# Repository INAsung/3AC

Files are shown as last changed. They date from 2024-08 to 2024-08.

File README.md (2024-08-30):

# Three-alternative forced choice task (3AC)

### *Low cost implementation of three-alternative forced choice task with Arduino mega 2560 &amp; 3D printing*

KakaoTalk_20240830_165530499

---
### *What is 3AC?*
그림1

- 3AC is extended version of conventional two-alternative forced choice task. 
- 3AC task comprises two phases:
	- i) blind tasting of either a pure tastant or mixture (e.g., sweet, salty, or sweet-salty mixture)
	- ii) selection of one of the three bottles corresponding to the tasted solution.

- **A servo motor** switches the tastant solution provided to the mouse for each trial. The liquids are never mixed because they flow through separate lines.
- **Linear actuators** move back and forth, allowing the mouse access to the lick spout for a limited time period.
- **DIY capacitive lickometer** detects and records licks.

- *This is the **first attempt** to match three choices to the three decision spouts.*
---

### *This repository includes:*
- Whole Arduino codes and 3D printing schematics for implementing 3AC behavioral apparatus
- Imaged guideline for making DIY capacitive sensor
- You can use this project for any task that requires the mouse to identify one of three possible options. (though, I developed it for a study on *taste mixture identification*.

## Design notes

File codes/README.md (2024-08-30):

# Description for task schedule and following Arduino codes

- ❗ You have to install additional Arduino libraries: **CapacitiveSensor (v 0.5.1)**, **Keypad (v 3.1.1)**
- **You should read each .ino files carefully and change each parameters as you want.** (pinmaps, servo motor's reducer ratio and encoder resolution, training schedules,  etc)

- **Tip for preventing choice bias**: Mice tend to lick the closest spout, so each spouts should be placed equally distant from target position.

- from stage3, I added keypad codes for convenience. (refer to code)
---

|name | explanation |expected period|
|:--:|:--:|:--:|
|stage1 |only central spouts move, give water unconditionally | 1~2 days|
|stage2 | only lateral spouts move, give water when lick is detected (choice should be counterbalanced) | 3 days
|stage3 |both lateral spouts and central spout move. give water when lick is deteced (choice should be counterbalanced) |5~7 days
|stage4|central spout come in and give water unconditionally. then, both lateral spouts and central spout come in and give water when lick is detected|1~2 days
|stage5 (semi-3AC)|easy version of 3AC. Sampling liquid does not change until the mouse makes three consecutive right choices or ten right choices.|3~4 weeks
|stage6 (real 3AC)| now, let's start 3AC task! (sampling liquid will be randomized for each trials) | 1 week

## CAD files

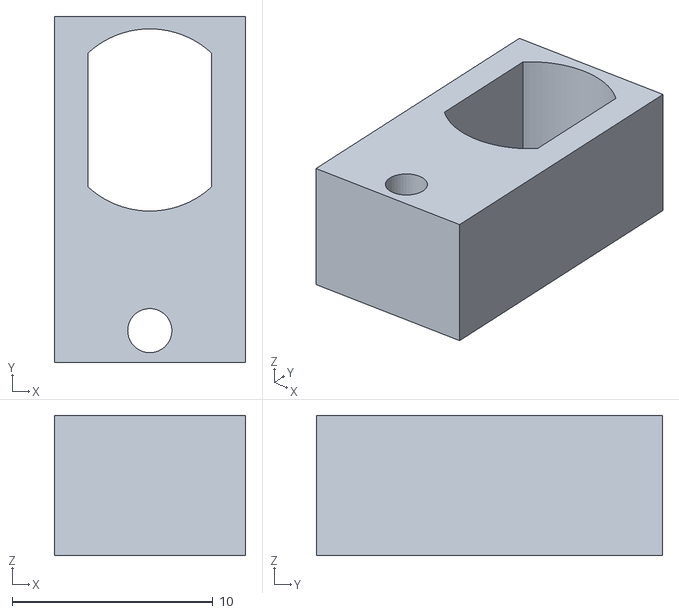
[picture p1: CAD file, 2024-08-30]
assembly/accessory/LATERAL_HOLDER.stl
9.52 x 17.3 x 7.00

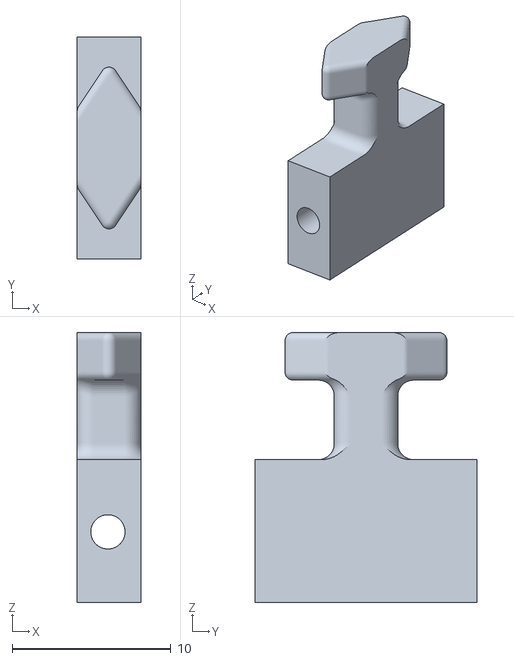
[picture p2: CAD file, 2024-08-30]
assembly/essential/CENTRAL_SAMPLING_HOLDER_SHORT.stl
4.00 x 14.0 x 17.0

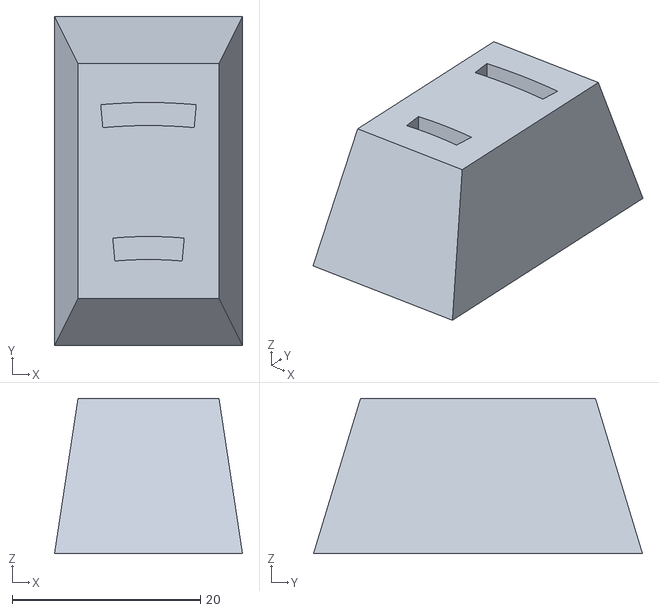
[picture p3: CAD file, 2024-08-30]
assembly/accessory/SPOUT_SELECTOR_SUPPORT_EXTENDER.stl
20.0 x 35.0 x 16.5

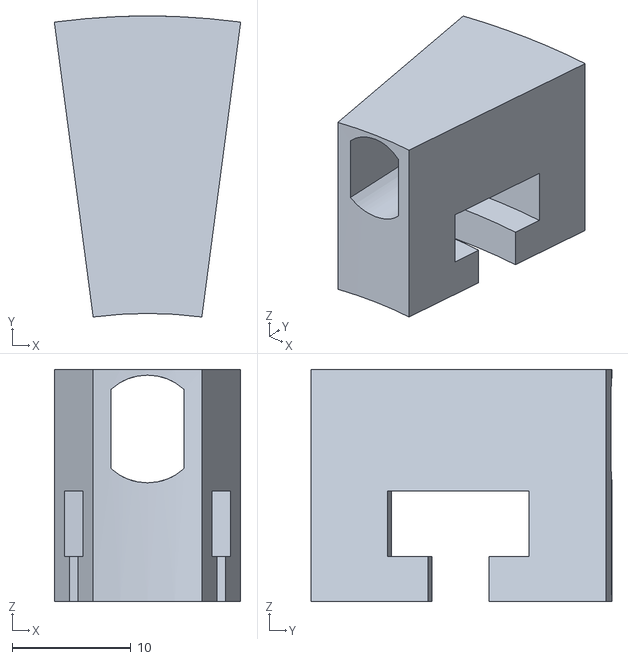
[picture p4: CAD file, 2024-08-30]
assembly/essential/MOTOR_CONNECTOR_THICK.stl
15.7 x 25.3 x 19.5

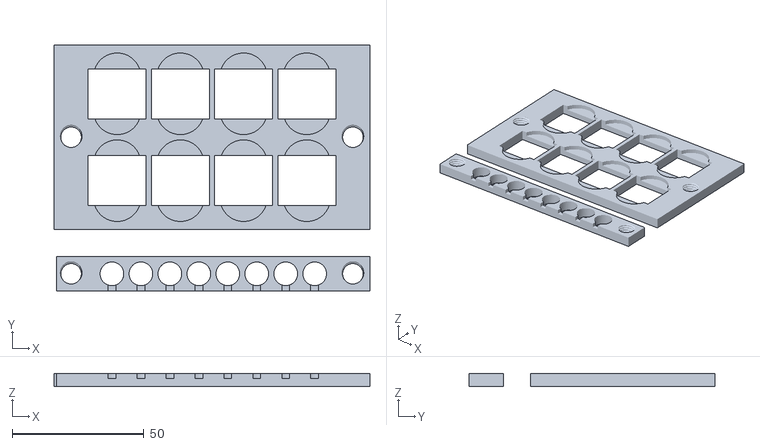
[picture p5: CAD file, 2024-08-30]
assembly/accessory/HOLDERS.stl
120.0 x 93.4 x 5.00

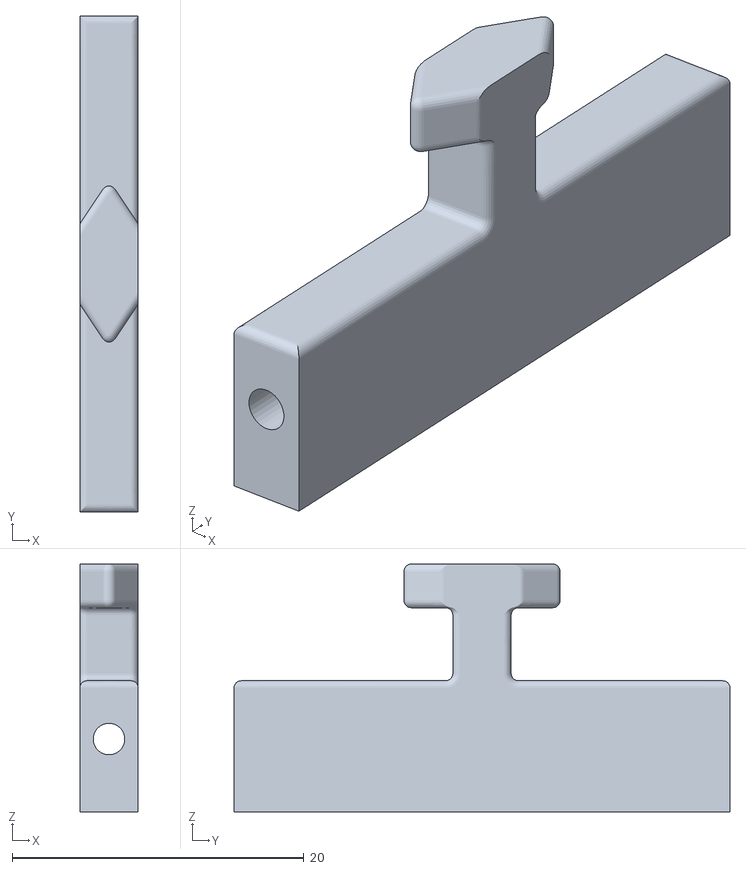
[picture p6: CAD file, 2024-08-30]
assembly/essential/CENTRAL_SAMPLING_HOLDER_LONG.stl
4.00 x 34.0 x 17.0

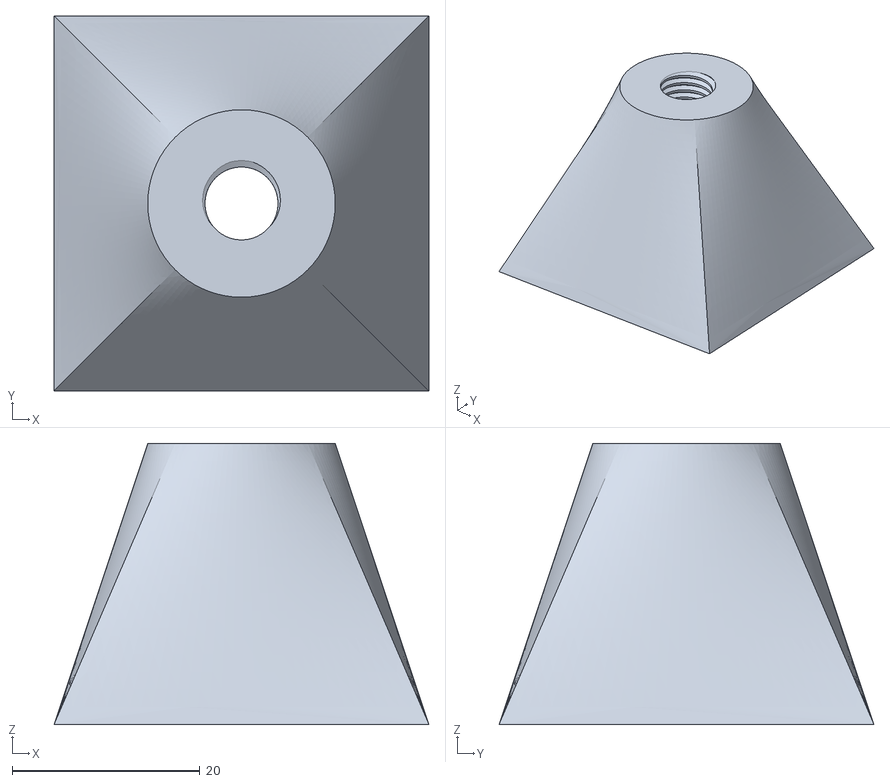
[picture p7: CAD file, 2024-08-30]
assembly/accessory/BASE.stl
40.0 x 40.0 x 30.0

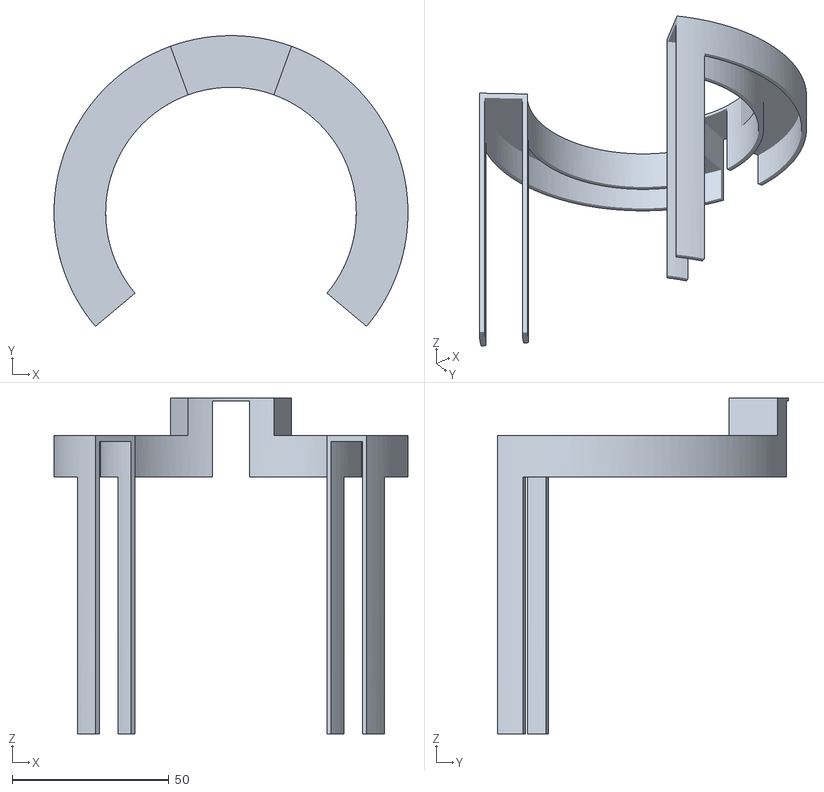
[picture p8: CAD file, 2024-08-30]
assembly/essential/SPOUT_SELECTOR_SUPPORT_THIN.stl
113.0 x 92.8 x 107.2

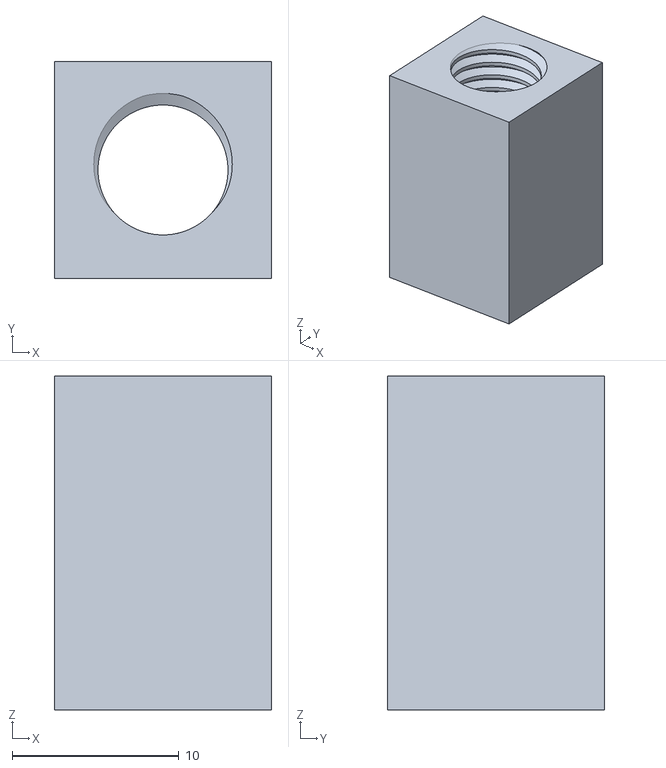
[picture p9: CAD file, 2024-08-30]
assembly/accessory/NAIL_EXTENDER.stl
13.0 x 13.0 x 20.0

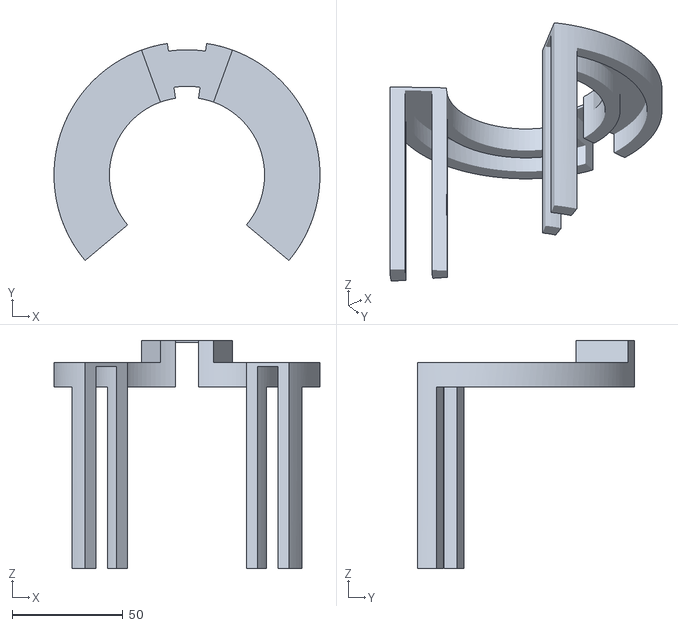
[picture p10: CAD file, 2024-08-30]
assembly/essential/SPOUT_SELECTOR_SUPPORT_THICK.stl
120.0 x 97.9 x 103.0

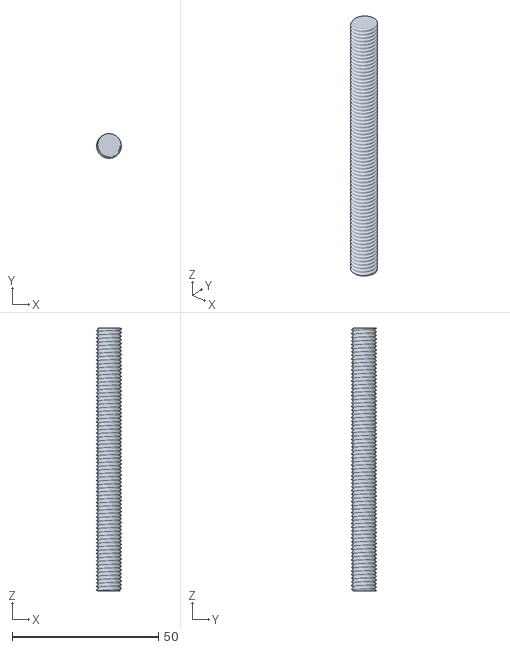
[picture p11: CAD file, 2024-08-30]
assembly/accessory/NAIL_90mm.stl
8.47 x 8.47 x 90.0

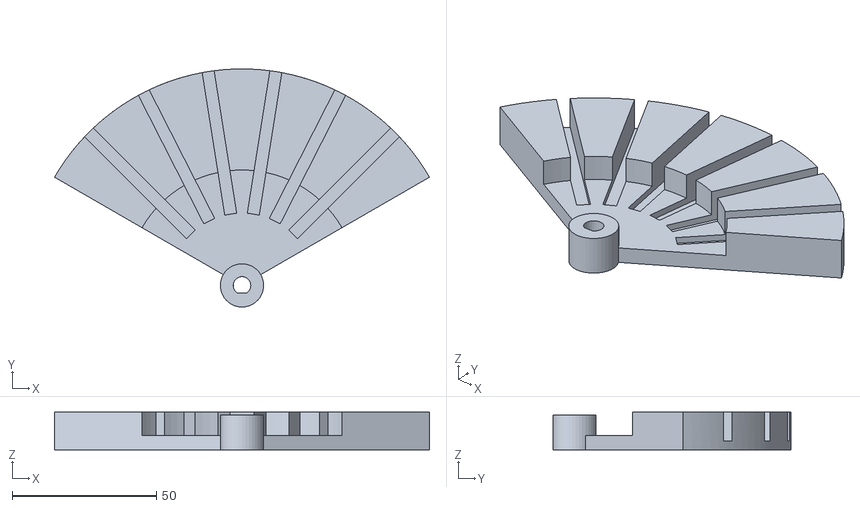
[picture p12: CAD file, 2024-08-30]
assembly/essential/SPOUT_SELECTOR_SHORT.stl
129.9 x 82.5 x 13.0

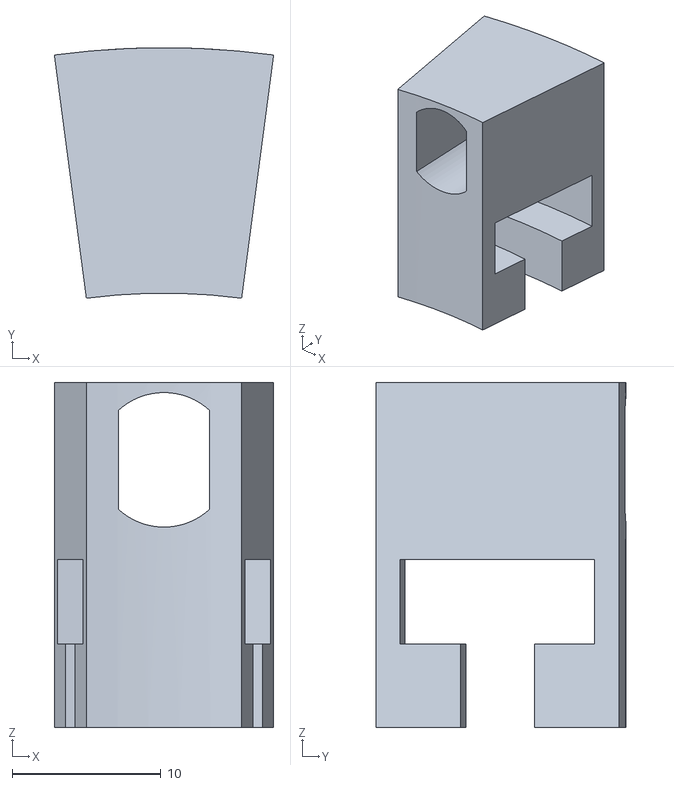
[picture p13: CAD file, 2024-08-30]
assembly/essential/MOTOR_CONNECTOR_THIN.stl
14.7 x 16.8 x 23.2

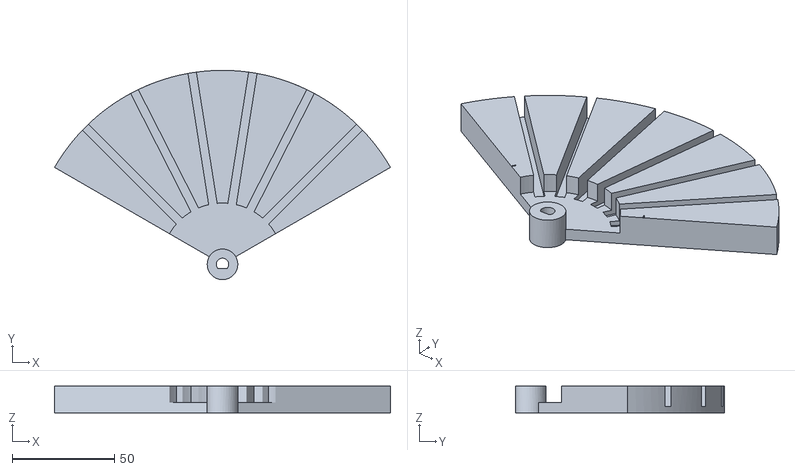
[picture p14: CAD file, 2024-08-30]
assembly/essential/SPOUT_SELECTOR_LONG.stl
164.5 x 102.5 x 13.0

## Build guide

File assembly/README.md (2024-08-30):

# Description for behavioral apparatus assembly & 3D printing

## General info

very grateful to Seoul National University Hadong idea factory...

+ 3D printing machine: one of 3D WOX DP200, DP103 or 2X
+ layer: 0.15mm 
+ program: Autodesk Fusion, 3DWOX Desktop x64

❗ proper post-processing is required. (I mostly used sand paper and soldering iron)

💡 If you need .f3d file, please contact.

📃 **The PDF file includes assembly images and detailed instructions for a simple capacitive lickometer.**

## What you need

### Key devices
|name|for what?|ea.|note|
|:---:|:---:|:---:|:---:|
|arduino mega 2650|main controller|1||
|linear actuator|liquid delivery|4|100mm range, 15mm/s model. I bought it from AliExpress, so I don't know exact model name|
|RB-35GM W/EC|servo motor with encoder for spout selection|1|https://www.dnjmall.com/goods/goods_list.php?cateCd=009|
|LHDA1231115H|solenoid valve for liquid control|10|from The LEE company|
|GJ-5FA-L [SY-SSR01]|DC to DC SSR for liquid control|10||
|L293D(DIP)|motor driver for linear actuator|3||

In addition, you will need enough amount of blunt needle(liquid spout for mouse), silicon tubing, arduino 4*4 keypad (for convenience), 2M ohmn resistors(for manual lickometer), and 12V DC power supply.

## Assembly
I mostly used **blu tack** for overall assembly.

- **Essential folder** contains essnetial parts for spout selection and delivery
  - There are thin/thick, long/short versions. (schematics are same, only length is different.)
  - I used thin and short versions, but newly made long and thick version to add precision.
  - It is okay to use thin and short versions, but if there occurs some errors, please consider long and thick versions. 

- **Accessory folder** contains liquid delivery tower, motor supporter, etc.

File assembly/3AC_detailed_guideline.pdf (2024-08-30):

## 1. Simple capacitive lickometer

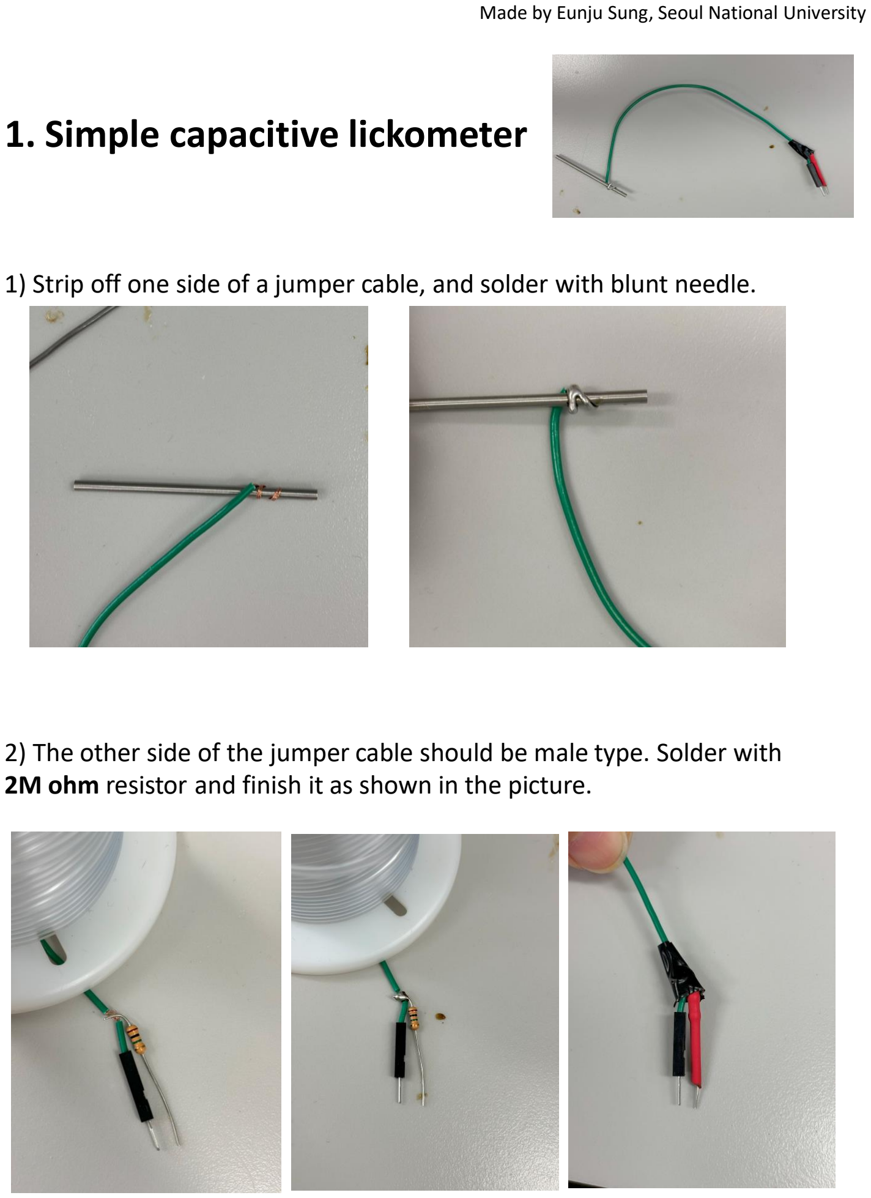
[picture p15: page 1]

Made by Eunju Sung, Seoul National University

1) Strip off one side of a jumper cable, and solder with blunt needle.
2) The other side of the jumper cable should be male type. Solder with 2M ohm resistor and finish it as shown in the picture.

### 1) Overall assembly

## 2. Behavioral apparatus assembly

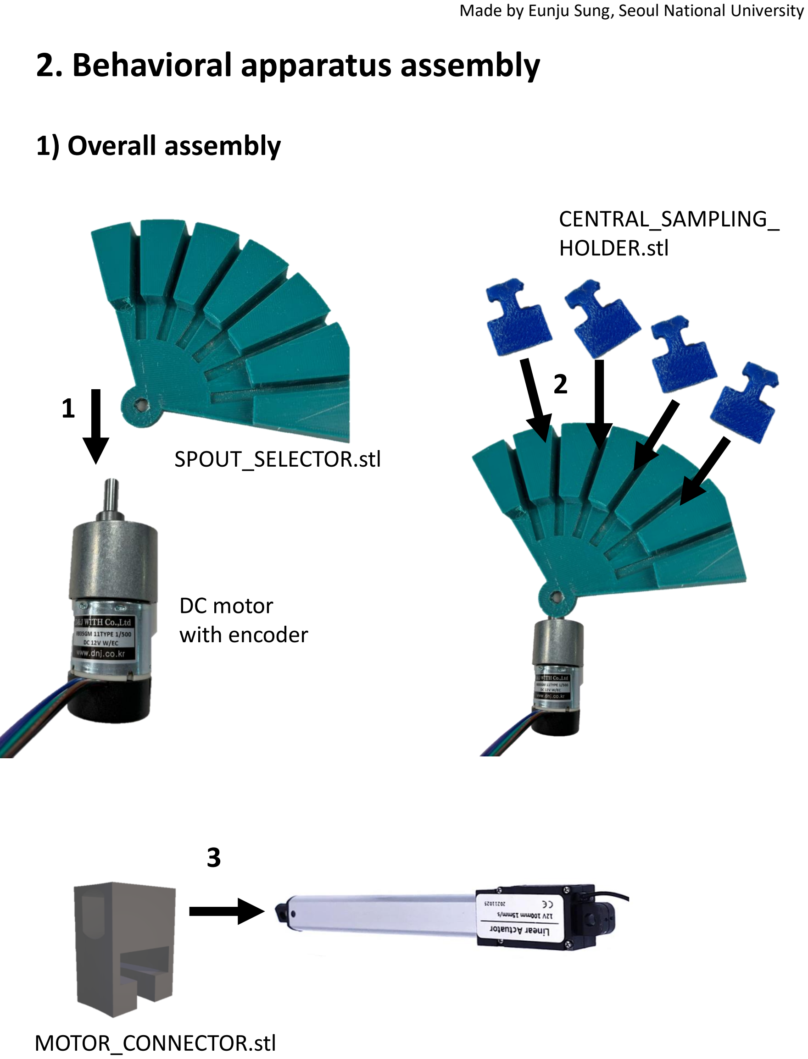
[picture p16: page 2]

1

DC motor
with encoder

SPOUT_SELECTOR.stl

2

CENTRAL_SAMPLING_
HOLDER.stl

3

MOTOR_CONNECTOR.stl

4

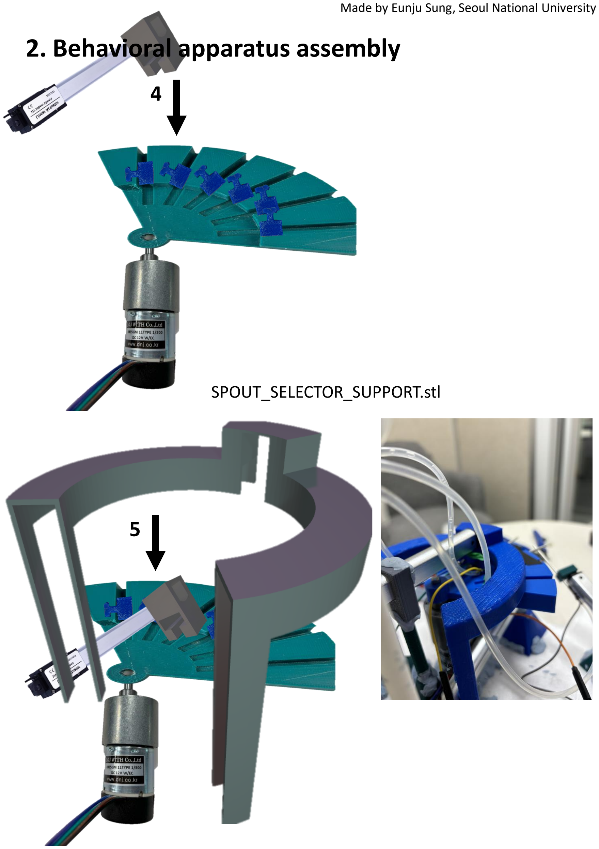
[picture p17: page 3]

SPOUT_SELECTOR_SUPPORT.stl

5

### 6. Place lateral motors and

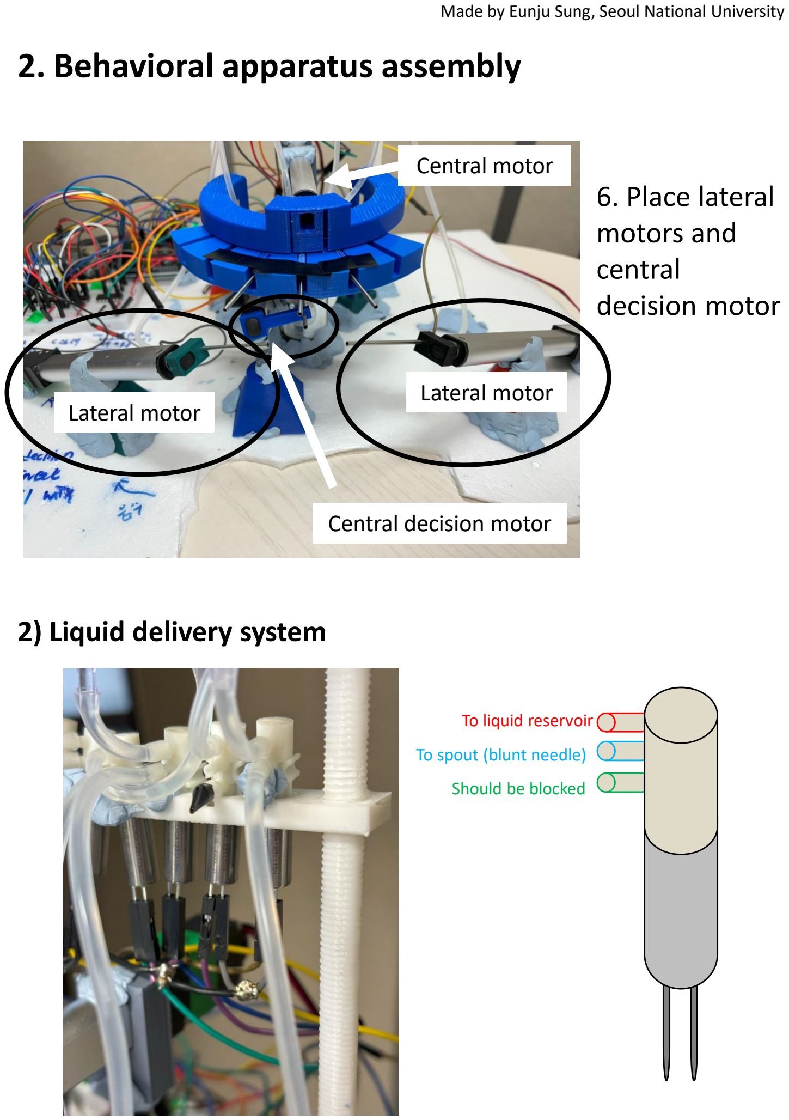
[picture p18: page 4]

### 2) Liquid delivery system

To liquid reservoir

Should be blocked

To spout (blunt needle)

### central decision motor

Lateral motor

Lateral motor

Central decision motor

Central motor

### 3) Spout location

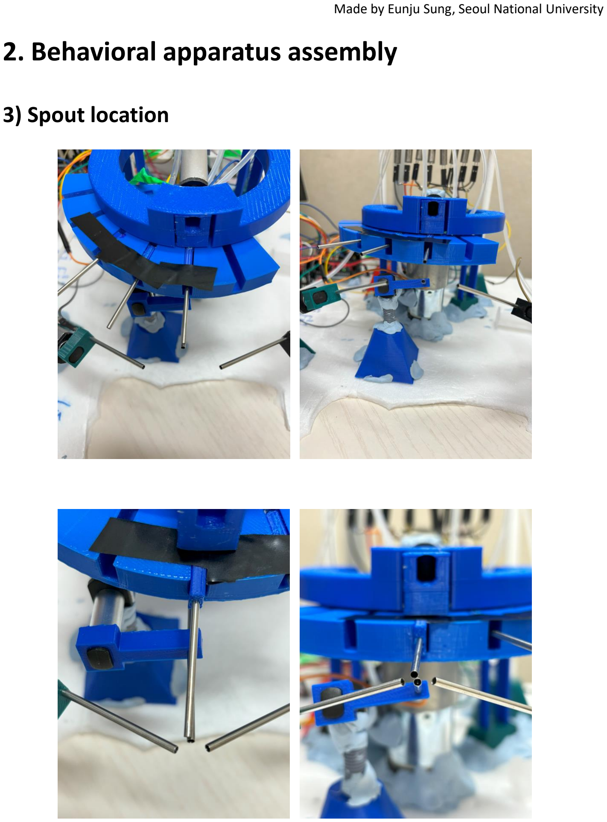
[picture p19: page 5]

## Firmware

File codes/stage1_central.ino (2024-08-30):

#include <CapacitiveSensor.h>

// source code for 3 alternative choice task
// you have to define all configurations according to your setup
// before get started, you must have to calibrate lickometer and motor extension length
// for lickometer calibration, set 'print_lickometer_raw' true and set status -1. Then, see each spout's value, determine float central_threshold[6] & lateral_threshold[2].

// made by Eunju Sung

//////////////// pinmap configurations ////////////////////
// motors (output)
const int lateral1A = 22 ;
const int lateral1B = 23 ;
const int lateral2A = 24 ;
const int lateral2B = 25 ;
const int centralA = 26 ;
const int centralB = 27 ;
const int steppin = 28 ;
const int dirpin = 29;

// solenoid valve control (output)
const int lateral_valve1 = 14;
const int lateral_valve2 = 15;
const int central_valve1 = 16;
const int central_valve2 = 17;
const int central_valve3 = 18;
const int central_valve4 = 19;
const int central_valve5 = 20;
const int central_valve6 = 21;

// lickometers (input)
// smaller number - resistor (red line) / bigger number - wire
const int lickL1A = 38;
const int lickL1B = 39;
const int lickL2A = 40;
const int lickL2B = 41;
const int lick1A = 42;
const int lick1B = 43;
const int lick2A = 44;
const int lick2B = 45;
const int lick3A = 46;
const int lick3B = 47;
const int lick4A = 48;
const int lick4B = 49;
const int lick5A = 50;
const int lick5B = 51;
const int lick6A = 52;
const int lick6B = 53;
CapacitiveSensor lickL1 = CapacitiveSensor(lickL1A, lickL1B);
CapacitiveSensor lickL2 = CapacitiveSensor(lickL2A, lickL2B);
CapacitiveSensor lick1 = CapacitiveSensor(lick1A, lick1B);
CapacitiveSensor lick2 = CapacitiveSensor(lick2A, lick2B);
CapacitiveSensor lick3 = CapacitiveSensor(lick3A, lick3B);
CapacitiveSensor lick4 = CapacitiveSensor(lick4A, lick4B);
CapacitiveSensor lick5 = CapacitiveSensor(lick5A, lick5B);
CapacitiveSensor lick6 = CapacitiveSensor(lick6A, lick6B);
CapacitiveSensor lateral_lickometers[2] = {lickL1, lickL2};
CapacitiveSensor central_lickometers[6] = {lick1, lick2, lick3, lick4, lick5, lick6};
//////////////////////////////////////////////////////


//////////////// output flags  ////////////////////
int status= 0; // -1 for lickometer calibration, 0 for training
bool print_lickometer_raw = true; // for lickometer calibration ## don't set it false. lickometers go wrong..
//////////////////////////////////////////////////////////////


//////////////// training configurations ////////////////////
// spout setting
const int central_reward = 3; // index from zero. spout for central decision
const int central_reward_pin = 19; // see above pinmap
bool lateral_enabled[2] = {false, false};
bool central_enabled[6] = {false, false, false, true, false, false};// do not set true for central_reward spout
const int lick_refractory_tick = 2; // cannot detect new lick for {lick_refractory_tick} ticks (sometimes capsense report single touch as two touch...)
const int capsensor_sensitivity = 40;
float central_threshold[6] = {50, 50, 80, 80, 50, 50};
float lateral_threshold[2] = {100, 50};
const float threshold_default = 10000000;

// trial schedule (unit: milli sec)
const int trial = 60; // number of trial in one session
const float ready2go = 5*1e3;
const float ITI = 15*1e3;
const float valveopen = 0.05*1e3;
const float valve2valve = 0.2*1e3;
const int samplingnum = 1; // give reward 'rewardnum' times, time gap between each delivery is 'valve2valve' 
const float sampling_offset = 0.5*1e3; // time for delay between spout extrude and sampling liquid delivery
const float central_ex = 1.5*1e3; // should be measured according to the distance you want to extrude
const float central_in = 1.6*1e3; // should be measured according to the distance you want to extrude
const float lateral_ex = 1.5*1e3; // should be measured according to the distance you want to extrude
const float lateral_in = 1.5*1e3; // should be measured according to the distance you want to extrude
int bottle_select_step = 160;// for 18 degree
const float start2central_in = 0*1e3;
///////////////////////////////////////////////////////

// 1. start, wait for start2central_in
// 2. central motor start to go forward, motor on for central_ex
// 3. give water unconditionally. valve open for valveopen
// 4. central motor goes back, motor on for central_in

//////// trial parameters (renewed every trial) ////////
unsigned long status_start_time = 0;
unsigned long trial_start_time = 0;
unsigned long now_time = 0;
int trial_count = 1;
int sampling_count = 0;
unsigned long time_consumed = 0; // time consumed for moving step motor (spout selection) 

struct Result{
  bool lickstarted = false;
  bool nowlick = false;
  long lickthres = threshold_default;
  int tick2lick = -1;
};

Result central_lick_status[6];
Result lateral_lick_status[2];
long central_vals_now[6] = {0};
long lateral_vals_now[2] = {0};
long central_vals_prev[6] = {0};
long lateral_vals_prev[2] = {0};
int central_lick_cnt[6] = {0};
int lateral_lick_cnt[2] = {0};
float central_prev_lick_started[6] = {0};
float lateral_prev_lick_started[2] = {0};
//////////////////////////////////////////////////////



////////////  define utility functions  //////////////
void delay_sec(int delay_millisec){
  delay(delay_millisec * 1000);
}

void trial_printer(int trial_count, unsigned long now_time){
  Serial.println("");
  Serial.println("////////////////////////////////////////////////////////////////////////////////////");
  Serial.println(String("//////////     Trial #" + String(trial_count) + " started.  //////////" ));
  Serial.println("////////////////////////////////////////////////////////////////////////////////////");
}

void decision_printer(int lateral_choice, int answer, char outcome){
  Serial.println(String("decision: " + String(lateral_choice) + " answer: " + String(answer) + ". outcome: " + String(outcome) ));
}

Result detect_lick(bool flag, long now_val, long prev_val, long lickthres, bool nowlick, int tick2lick, int thres) {
  Result result;

  // clock tick from start of the lick
  // tick2lick=-1 : ready to lick
  if (tick2lick > -1 && (tick2lick < lick_refractory_tick || tick2lick == lick_refractory_tick)) {
    tick2lick += 1;
  } else if (tick2lick > lick_refractory_tick) {
    tick2lick = -1;
  }
  result.tick2lick = tick2lick;

  // detect lick
  // lick started
  if (tick2lick == -1 && nowlick == false && now_val - prev_val > thres) {
    result.nowlick = true;
    result.lickthres = now_val;
    result.lickstarted = true;
    result.tick2lick = 0;
  }
  // prolonged lick
  else if (nowlick == true && now_val > lickthres) {
    result.nowlick = true;
    result.lickstarted = false;
    result.lickthres = lickthres;
  } else if (nowlick == true && (now_val < lickthres || now_val == lickthres)) {
    result.nowlick = false;
    result.lickstarted = false;
    result.lickthres = threshold_default;
  }
  return result;
}

void print_lick(bool flag, char* prefix, int idx, bool lickstarted, int& cnt, float& prev_lick_started, unsigned long now_time) {
  String name;
  name = String(String(prefix) + String(idx));
  if (flag && lickstarted) {
    cnt += 1;
    Serial.print(name);
    Serial.print(" lick detected!     count: ");
    Serial.print(cnt);
    Serial.print("     lick2lick: ");
    Serial.println(now_time - prev_lick_started);
    prev_lick_started = now_time;
  }
}

//////////////////////////////////////////////////////


void setup() {
// pin I/O 
pinMode ( lateral1A, OUTPUT ) ;
pinMode ( lateral2A, OUTPUT ) ;
pinMode ( lateral1B, OUTPUT ) ;
pinMode ( lateral2B, OUTPUT ) ;
pinMode ( centralA, OUTPUT ) ;
pinMode ( centralB, OUTPUT ) ;
pinMode ( steppin, OUTPUT ) ;
pinMode ( dirpin, OUTPUT ) ;

pinMode ( lateral_valve1, OUTPUT );
pinMode ( lateral_valve2, OUTPUT );
pinMode ( central_valve1, OUTPUT ) ;
pinMode ( central_valve2, OUTPUT ) ;
pinMode ( central_valve3, OUTPUT ) ;
pinMode ( central_valve4, OUTPUT ) ;
pinMode ( central_valve5, OUTPUT ) ;
pinMode ( central_valve6, OUTPUT ) ;

// begin serial
Serial.begin(57600);

// seed
randomSeed(analogRead(0));

// setup for lickometer (begin capsensors)
  for (int i=0; i<2; i++){
    if (lateral_enabled[i]){
      lateral_lickometers[i].set_CS_AutocaL_Millis(0xFFFFFFFF);
      Serial.print(String("\t" + String("lateral") + String(i+1) + "\t" + String(lateral_threshold[i])));
    }
  }
  for (int i=0; i<6; i++){
    if (central_enabled[i]){
      central_lickometers[i].set_CS_AutocaL_Millis(0xFFFFFFFF);
      Serial.print(String("\t" + String("central") + String(i+1) + "\t" + String(central_threshold[i])));
    }
  }
  Serial.println("");
  Serial.println("/////////////////////////////////////////////////////////");
  Serial.println("/////////          session started              /////////");
  Serial.println("/////////////////////////////////////////////////////////");
}
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

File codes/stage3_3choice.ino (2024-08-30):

#include <CapacitiveSensor.h>
#include <Key.h>
#include <Keypad.h>

// source code for 3 alternative choice task
// you have to define all configurations according to your setup
// before get started, you must have to calibrate lickometer and motor extension length
// for lickometer calibration, set 'print_lickometer_raw' true and set status -1. Then, see each spout's value, determine float central_threshold[6] & lateral_threshold[2].

// made by Eunju Sung

//////////////// pinmap configurations ////////////////////
// motors (output)
const int lateral1A = 22;
const int lateral1B = 23;
const int lateral2A = 24;
const int lateral2B = 25;
const int centralA = 26;
const int centralB = 27;
const int encoderPinA = 2;
const int encoderPinB = 3;
const int motorDirPin = 8;  // L298 Input 1
const int motorPWMPin = 9;  // L298 Input 2
const int central_dA = 6;
const int central_dB = 7;


// solenoid valve control (output)
const int lateral_valve1 = 14;
const int lateral_valve2 = 15;
const int central_valve1 = 16;
const int central_valve2 = 17;
const int central_valve3 = 18;
const int central_valve4 = 19;
const int central_valve5 = A14;
const int central_valve6 = 21;

// lickometers (input)
// smaller number - resistor (red line) / bigger number - wire
const int lickL1A = 32;
const int lickL1B = 33;
const int lickL2A = 36;
const int lickL2B = 37;
const int lick1A = 40;
const int lick1B = 41;
const int lick2A = 30;
const int lick2B = 31;
const int lick3A = 46;
const int lick3B = 47;
const int lick4A = 48;
const int lick4B = 49;
const int lick5A = 50;
const int lick5B = 51;
const int lick6A = 52;
const int lick6B = 53;
CapacitiveSensor lickL1 = CapacitiveSensor(lickL1A, lickL1B);
CapacitiveSensor lickL2 = CapacitiveSensor(lickL2A, lickL2B);
CapacitiveSensor lick1 = CapacitiveSensor(lick1A, lick1B);
CapacitiveSensor lick2 = CapacitiveSensor(lick2A, lick2B);
CapacitiveSensor lick3 = CapacitiveSensor(lick3A, lick3B);
CapacitiveSensor lick4 = CapacitiveSensor(lick4A, lick4B);
CapacitiveSensor lick5 = CapacitiveSensor(lick5A, lick5B);
CapacitiveSensor lick6 = CapacitiveSensor(lick6A, lick6B);

CapacitiveSensor lateral_lickometers[2] = { lickL1, lickL2 };
CapacitiveSensor central_lickometers[6] = { lick1, lick2, lick3, lick4, lick5, lick6 };

// keypad (input)
const byte ROWS = 4;
const byte COLS = 4;

char hexaKeys[ROWS][COLS] = {
  { '0', '1', '2', '3' },
  { '4', '5', '6', '7' },
  { '8', '9', 'a', 'b' },
  { 'c', 'd', 'e', 'f' }
};
byte rowPins[ROWS] = { A4, A5, A6, A7 };
byte colPins[COLS] = { A0, A1, A2, A3 };

char customKey;

Keypad customKeypad = Keypad(makeKeymap(hexaKeys), rowPins, colPins, ROWS, COLS);
//////////////////////////////////////////////////////


//////////////// output flags  ////////////////////
int status = 0;                     // -1 for lickometer calibration, 0 for training
bool print_lickometer_raw = false;  // for lickometer calibration ## don't set it false. lickometers go wrong..
//////////////////////////////////////////////////////////////


//////////////// training configurations ////////////////////
// spout setting
const int initial_central_spout = 3;  // index from zero
const int central_decision = 1;       // index from zero. spout for central decision
const int central_decision_pin = 17;  // see above pinmap
bool lateral_enabled[2] = { true, true };
bool central_enabled[6] = { false, true, false, false, false, false };
bool central_choices[6] = { false, false, false, false, false, false };  // set central decision pin false.
int answerbook[6] = { 0, 0, 3, 2, 1, 0 };
int next_thres = 4;
const int lick_refractory_tick = 2;  // cannot detect new lick for {lick_refractory_tick} ticks (sometimes capsense report single touch as two touch...)
const int capsensor_sensitivity = 40;
float central_threshold[6] = { 60, 70, 60, 70, 70, 50 };
float lateral_threshold[2] = { 50, 100 };
const float threshold_default = 10000000;

// trial schedule (unit: milli sec)
const int trial = 500;  // number of trial in one session
const float ready2go = 5 * 1e3;
const float ITI = 5 * 1e3;
const float timeout = 6 * 1e3;
const float reward_valveopen = 0.1 * 1e3;
const float sampling_valveopen = 0.07 * 1e3;
const int samplingnum = 1;  // give delivery 'samplingnum' times, time gap between each delivery is 'valve2valve'
const float time4decision = 2 * 1e3;
const float wait4nolick = 1 * 1e3;
const float valve_offset = 0.5 * 1e3;  // time for delay between spout extrude and sampling liquid delivery
const float central_ex = 1.3 * 1e3;    // should be measured according to the distance you want to extrude
const float central_in = 1.55 * 1e3;   // should be measured according to the distance you want to extrude
const float central_d_ex = 1.5 * 1e3;  // should be measured according to the distance you want to extrude
const float central_d_in = 1.6 * 1e3;  // should be measured according to the distance you want to extrude
const float lateral_ex = 1.48 * 1e3;   // should be measured according to the distance you want to extrude
const float lateral_in = 1.6 * 1e3;    // should be measured according to the distance you want to extrude
int bottle_select_step = 160;          // for 18 degree. M1, M2, M3 HiGH (1/16)
int stepmotor_offset = 40;             // step motor has little offset if the direciton change. should be measured carefully.
const float start2central_in = 0 * 1e3;
//////////////////////////////////////////////////////

// 1. start, wait for start2central_in
// 2. lateral motors and central decision motor start to go forward, motor on for lateral_ex and central_d_ex each
// 3. give water when a lick is detected. valve open for valveopen
// * to prevent bias, water is not given for dominant choice (>70% choice or more than 4 consecutive choice)
// * if the mouse does not stick to one spout within a trial, lateral motors go back immediately.
// 4. all motors go back, motor on for lateral_in and central_d_in each
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
